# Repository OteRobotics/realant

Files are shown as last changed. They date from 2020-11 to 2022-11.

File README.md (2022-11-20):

RealAnt
=======

The RealAnt robot platform from Ote Robotics is designed for real-world 
reinforcement learning research and development. It is a complete solution 
with a web camera based tracking system. It is aimed to be a low-cost starting
point for anybody interested in bringing reinforcement learning to practical
real robots.

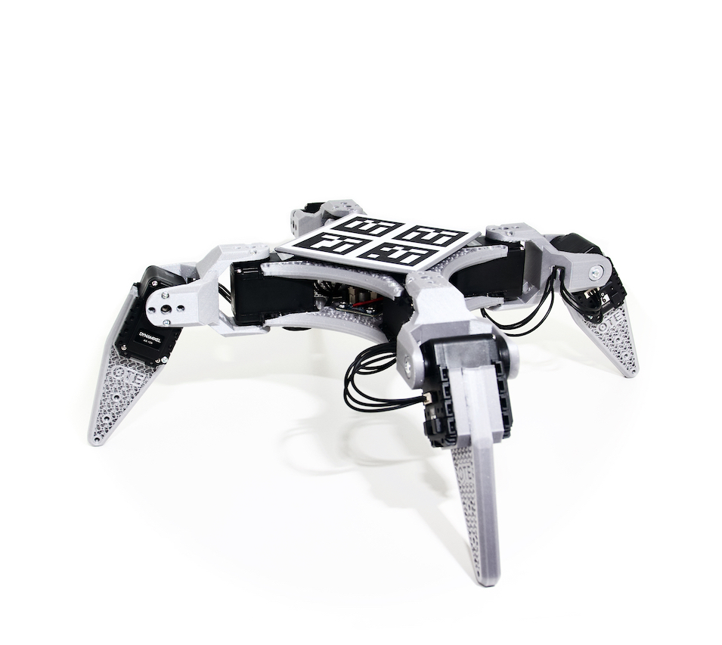
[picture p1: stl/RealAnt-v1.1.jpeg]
RealAnt-v1.1/v1.2


This repository provides 3D models and build instructions
for making your own RealAnt, firmware code for the robot microcontroller, and
Python code for the robot interface and ArUco tag based pose estimation.

If you want to get the robot ready assembled, you can buy them from
<https://shop.oterobotics.com>.

For an example implementation of reinforcement learning that learns
to stand, turn and walking, see <https://github.com/AaltoVision/realant-rl>.

# Getting Started

You can get to reinforcement learning in the real world with five steps:

1. Get or build your own RealAnt.
1. Calibrate and test the web camera for pose estimation.
1. Setup testing scene with adequate lighting.
1. Start Python Server scripts.
1. Start experiments.

## Get Your RealAnt

If you want to get the robot ready assembled, you can buy them from
<https://shop.oterobotics.com>.

To build your own, you need to obtain 8 Robotis Dynamixel AX-12A's and
one Robotis OpenCM9.04A board + accessory set or Ote Robotics RealAnt
Main Board v1.2 with Arduino Nano 33 IoT (see `board_1.2` folder for
PCB gerbers, BOM, layout and schematics PDFs).  

For building, you need additionally some two-wire cable for power, 
a soldering iron, side cutters, a Phillips screwdriver and 
thread-locking fluid (such as Loctite blue).

The 3D model files are under `stl` folder. You need to print two
body torso plates and four leg assemblies.

For PrusaSlicer, use 20% gyroid infill, 0.2mm layer height, no top 
and bottom layers.

## RealAnt Main Board Firmware

For the OpenCM9.04A board, install Arduino and setup Robotis OpenCM9.04 board support,
and then upload the OpenCM9.04 firmware from `ant11_cmd_dxl` folder.

For the Ote Robotics RealAnt Main Board v1.2 with Arduino Nano 33 IoT, 
install Arduino and use firmware from `ant14_cmd_dxl_nano33iot` folder.
You also need to install the forked DynamixelSDK from this folder into
Arduino libraries.

## Pose Estimation Calibration and Testing

Print calibration chessboard from `markers` on
e.g. A4 and glue them to a flat surface (e.g. piece of cardboard). 
Print the calibration chessboard at 100% scale, this
produces 4cm chessboard pattern. (If you use a different scaling, change
`calibrate_camera.py` script's marker size accordingly.)
Clipping at the edges of the outermost squares doesn't matter,
as only the inner corners of the squares are used.

Capture various poses of the chessboard (15+ images)
with `capture.py` and then run `calibrate_camera.py`.
Move the position of the chessboard around, so that it would
cover the whole field of view of the camera. Tilting
the chessboard also can yield better calibration.
Make sure your chessboard poses are free from motion blur,
delete the ones that are blurry.

After this, run `calibrate_camera.py` to obtain `cam_calib.pkl` file.

```
# mkdir CAMERANAME
# cd CAMERANAME
# python ../capture.py
# python ../calibrate_camera.py 
```

After calibrating the camera, adjust `showaruco_board.py` such
that it uses the correct `cam_calib.pkl` file.

Print and attach reference and moving agent markers to 
floor and the ant, adjust their sizes in the `showaruco_board.py` script
and run the script to estimate distance. Make sure to use correct
camera calibration file.

```
# python showaruco_board.py
```

## Setup The Test Scene

Make sure you have adequate lighting so that there is no motion blur in
pose estimation during robot movement.

For example, 2x 50W LED floodlights rated at 3800 lumens 
mounted 1 m above the robot should yield around 3000 lux illuminance
at the robot level, which is enough for reinforcement learning purposes
with Logitech Brio 4K USB camera.

## Python Interface Server

For starting trials, start the following scripts in their own terminal windows:

```
# python antproxy.py         # zmq pub-sub communication proxy
# python ant_server.py       # server for serial communication to the physical ant
# python showaruco_board.py  # pose estimation
```

You might need to adjust `ant_server.py` for the correct serial port device.
It defaults to `/dev/ttyACM0` on Linux.

Test scripts:

```
# python ant_send_cmd.py     # send simple test movements to ant
```

## Reinforcement Learning

For an example implementation of reinforcement learning that learns
to stand, turn and walking, see https://github.com/AaltoVision/realant-rl.

Clone that repository, and then run the scripts:

```
# rollout_server.py             # random exploration & agent evaluation
# train_client.py --task walk   # train for walking
```

# Further Interface Implementation Details

The main components are

 * `antproxy.py` (the main pub-sub network proxy, this should work as-is, as it just receives and forwards packages as a message hub — just run this on the background),
 * `showaruco_board.py` (this sends orientation and location info) and
 * `ant_server.py` (this processes the s1...s8 servo commands, and sends joint position values and (optional) foot sensors).
 
The pub-sub network protocol is very simple.
Each message is a list of byte strings.
The beginning of the first string is the "topic" in ZMQ terms
(used with `zmq.SUBSCRIBE` to filter in messages, `""` receives everything):

 * `"cmd"` is a command that the `ant_server.py` receives. This takes a 
   multipart string argument that is forwarded to the firmware. 
   Currently supported commands are `"sN X sM Y ..."` where N,M = servo number
   in [1,8] and X,Y = angle setpoint in [224...800], 512 = middle,
   and `"reset"`, `"attach_servos"` and `"detach_servos"`.
 * `"{"` which is json data, which is used both for all measurements 
   (and recorded setpoints) from `ant_server.py` and also for 
   `showaruco_board.py` measurement packets.

# RealAnt Revision History

| Version | Description |
| --- | --- |
| RealAnt v1 | First version with FP04-2 hip joints and OpenCM9.04 microcontroller board |
| RealAnt v1.1 | Hip joints replaced with 3D printed ones, OpenCM9.04 microcontroller board |
| RealAnt v1.2 | Microcontroller board changed to Arduino Nano 33 IoT based one |

# Copyright and License

Unless otherwise noted, all source code, documentation and data in this
repository is Copyright (c) 2020 Ote Robotics Ltd and is licensed under
MIT license.

See LICENSE for details.

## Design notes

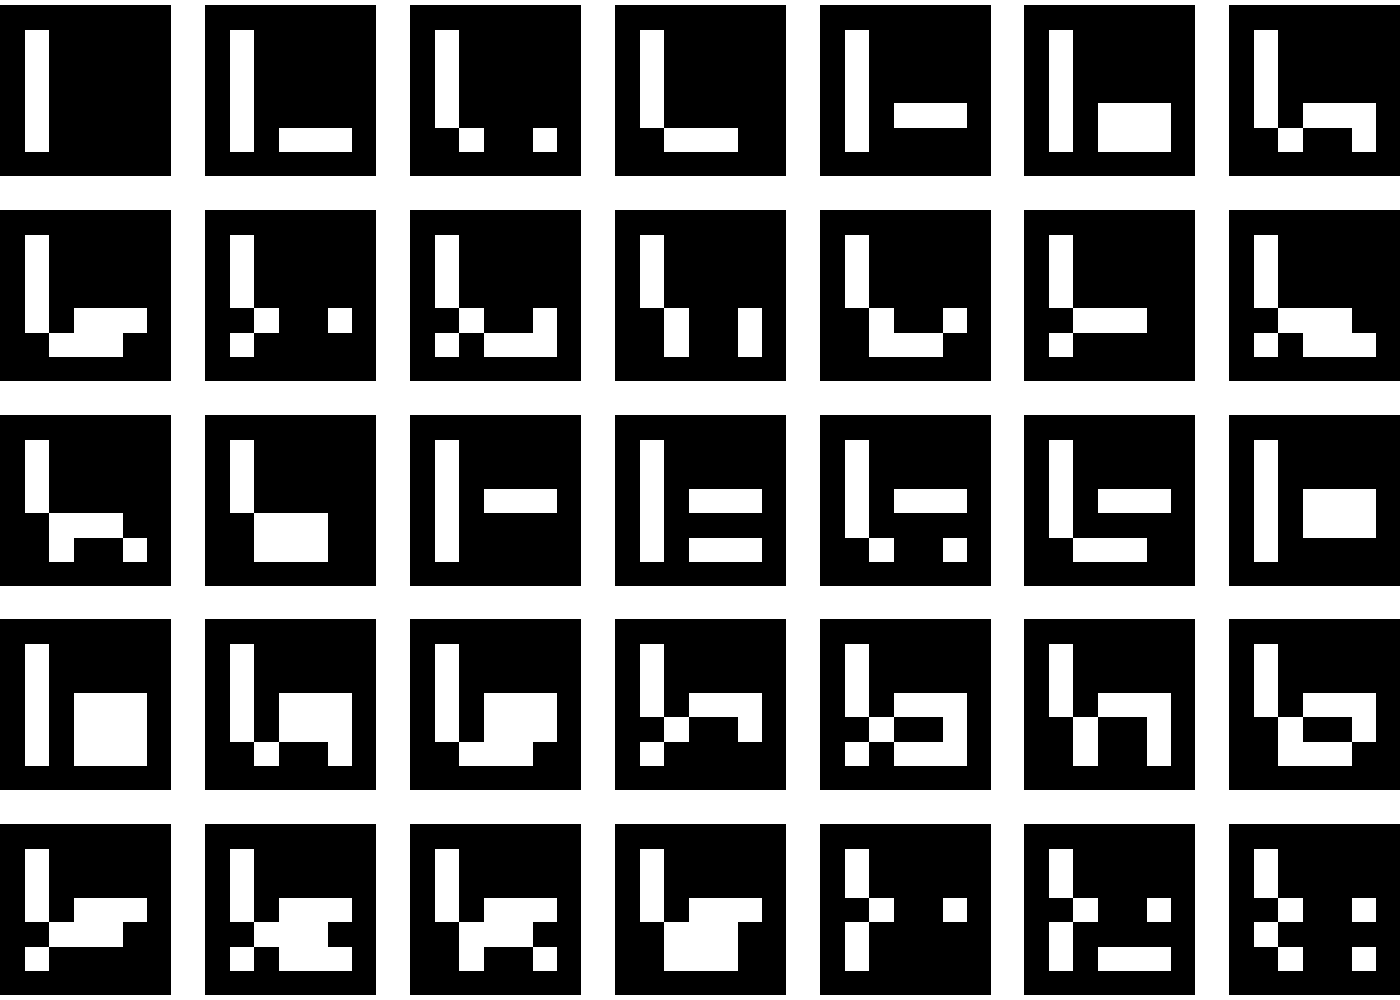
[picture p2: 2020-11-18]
markers/aruco_gridboard_big.png

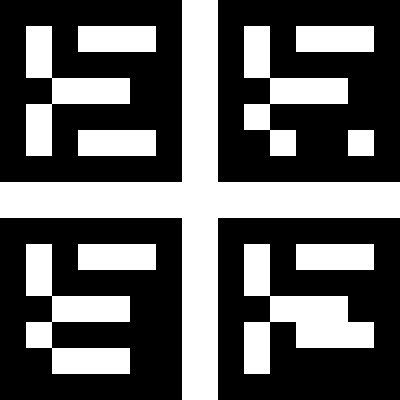
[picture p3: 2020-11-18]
markers/aruco_gridboard_small.png

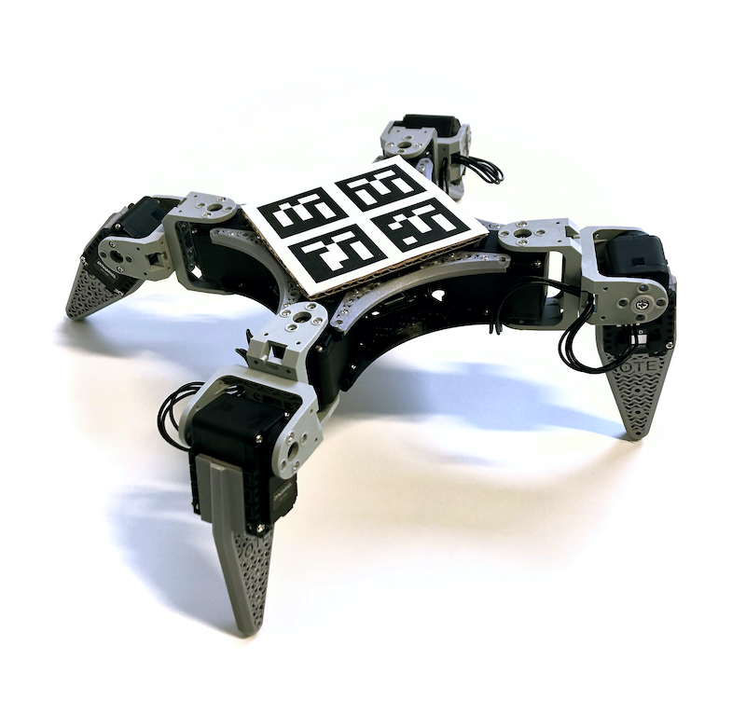
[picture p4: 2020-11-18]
stl/RealAnt-v1.jpeg

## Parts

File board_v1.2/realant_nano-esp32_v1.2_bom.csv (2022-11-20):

Source: | realant_nano_esp32.kicad_sch
Date: | 2022 August 14, Sunday 13:06:41
Tool: | Eeschema (6.0.0-0)
Generator: | /Applications/KiCad/KiCad.app/Contents/SharedSupport/plugins/bom_csv_grouped_by_value.py
Component Count: | 16
Individual Components:
Item | Qty | Reference(s) | Value | LibPart | Footprint | Datasheet
 |  | C1 | 0.1uF | Device:C | Capacitor_SMD:C_0805_2012Metric_Pad1.18x1.45mm_HandSolder | ~
 |  | C2 | 220uF | Device:C_Polarized | Capacitor_THT:CP_Radial_D6.3mm_P2.50mm | ~
 |  | C3 | 220uF | Device:C_Polarized | Capacitor_THT:CP_Radial_D6.3mm_P2.50mm | ~
 |  | J1 | DXL_CONN | connector:DXL_CONN | Connector_JST:JST_EH_B3B-EH-A_1x03_P2.50mm_Vertical
 |  | J2 | DXL_CONN | connector:DXL_CONN | Connector_JST:JST_EH_B3B-EH-A_1x03_P2.50mm_Vertical
 |  | J3 | DXL_CONN | connector:DXL_CONN | Connector_JST:JST_EH_B3B-EH-A_1x03_P2.50mm_Vertical
 |  | J4 | DXL_CONN | connector:DXL_CONN | Connector_JST:JST_EH_B3B-EH-A_1x03_P2.50mm_Vertical
 |  | R1 | 10k | Device:R | Resistor_SMD:R_0805_2012Metric_Pad1.20x1.40mm_HandSolder | ~
 |  | R2 | 10k | Device:R | Resistor_SMD:R_0805_2012Metric_Pad1.20x1.40mm_HandSolder | ~
 |  | R3 | 10k | Device:R | Resistor_SMD:R_0805_2012Metric_Pad1.20x1.40mm_HandSolder | ~
 |  | R4 | 5.1k | Device:R | Resistor_SMD:R_0805_2012Metric_Pad1.20x1.40mm_HandSolder | ~
 |  | U1 | ESP32-DevKitC | ESP32-Boards:ESP32-DevKitC | Espressif:ESP32-DevKitC | https://docs.espressif.com/projects/esp-idf/zh_CN/latest/esp32/hw-reference/esp32/get-started-devkitc.html
 |  | U2 | Arduino-NANO-33 | nano33iot:Arduino-NANO-33 | nano33iot:NANO_33_Socket | ~
 |  | U3 | 74LVC2G241DC | ICs:74LVC2G241DC | Package_SO:SSOP-8_2.95x2.8mm_P0.65mm | https://www.mouser.fi/datasheet/2/916/74LVC2G241-1319835.pdf
 |  | U4 | PWR_CONN | connector:PWR_CONN | Connector_Molex:Molex_Micro-Fit_3.0_43650-0200_1x02_P3.00mm_Horizontal
 |  | U5 | NCP1117-5.0_SOT223 | Regulator_Linear:NCP1117-5.0_SOT223 | Package_TO_SOT_SMD:SOT-223-3_TabPin2 | http://www.onsemi.com/pub_link/Collateral/NCP1117-D.PDF
Collated Components:
Item | Qty | Reference(s) | Value | LibPart | Footprint | Datasheet
1 | 1 | C1 | 0.1uF | Device:C | Capacitor_SMD:C_0805_2012Metric_Pad1.18x1.45mm_HandSolder | ~
2 | 2 | C2, C3 | 220uF | Device:C_Polarized | Capacitor_THT:CP_Radial_D6.3mm_P2.50mm | ~
3 | 4 | J1, J2, J3, J4 | DXL_CONN | connector:DXL_CONN | Connector_JST:JST_EH_B3B-EH-A_1x03_P2.50mm_Vertical
4 | 3 | R1, R2, R3 | 10k | Device:R | Resistor_SMD:R_0805_2012Metric_Pad1.20x1.40mm_HandSolder | ~
5 | 1 | R4 | 5.1k | Device:R | Resistor_SMD:R_0805_2012Metric_Pad1.20x1.40mm_HandSolder | ~
6 | 1 | U1 | ESP32-DevKitC | ESP32-Boards:ESP32-DevKitC | Espressif:ESP32-DevKitC | https://docs.espressif.com/projects/esp-idf/zh_CN/latest/esp32/hw-reference/esp32/get-started-devkitc.html
7 | 1 | U2 | Arduino-NANO-33 | nano33iot:Arduino-NANO-33 | nano33iot:NANO_33_Socket | ~
8 | 1 | U3 | 74LVC2G241DC | ICs:74LVC2G241DC | Package_SO:SSOP-8_2.95x2.8mm_P0.65mm | https://www.mouser.fi/datasheet/2/916/74LVC2G241-1319835.pdf
9 | 1 | U4 | PWR_CONN | connector:PWR_CONN | Connector_Molex:Molex_Micro-Fit_3.0_43650-0200_1x02_P3.00mm_Horizontal
10 | 1 | U5 | NCP1117-5.0_SOT223 | Regulator_Linear:NCP1117-5.0_SOT223 | Package_TO_SOT_SMD:SOT-223-3_TabPin2 | http://www.onsemi.com/pub_link/Collateral/NCP1117-D.PDF

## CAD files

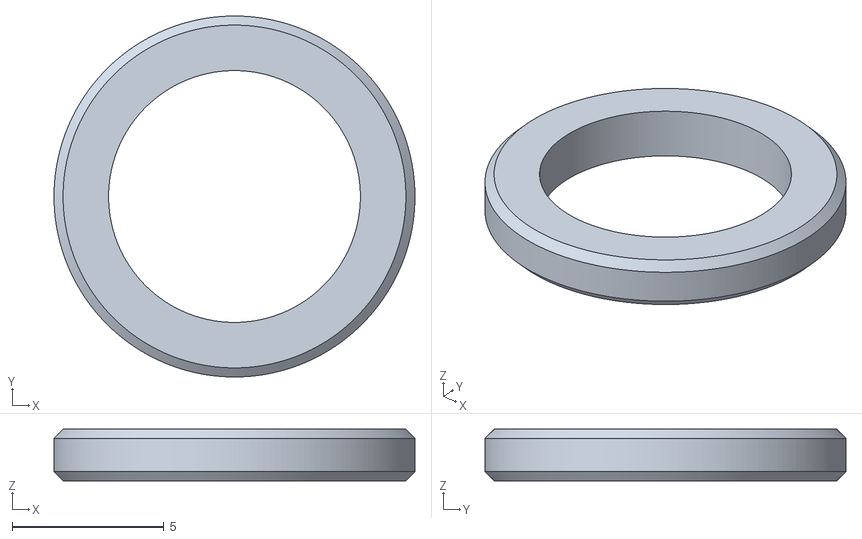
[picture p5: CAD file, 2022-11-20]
stl/joint_spacer_ring.stl
11.9 x 11.9 x 1.70

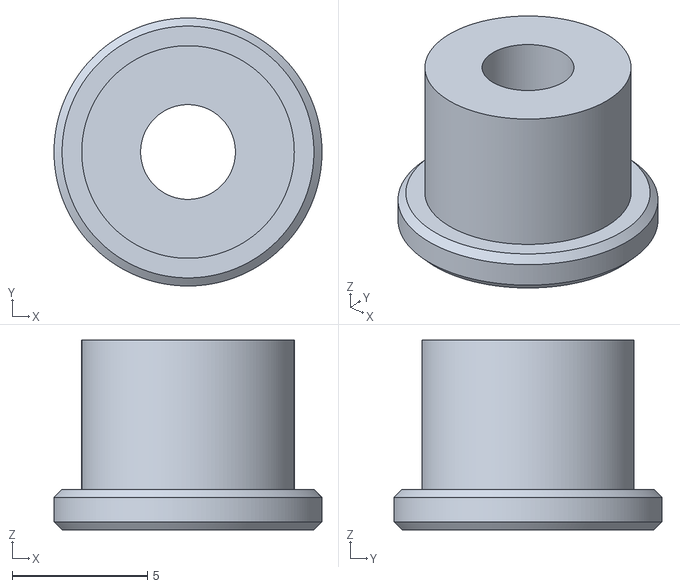
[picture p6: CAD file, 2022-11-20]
stl/joint_slide_bearing.stl
9.90 x 9.90 x 7.01

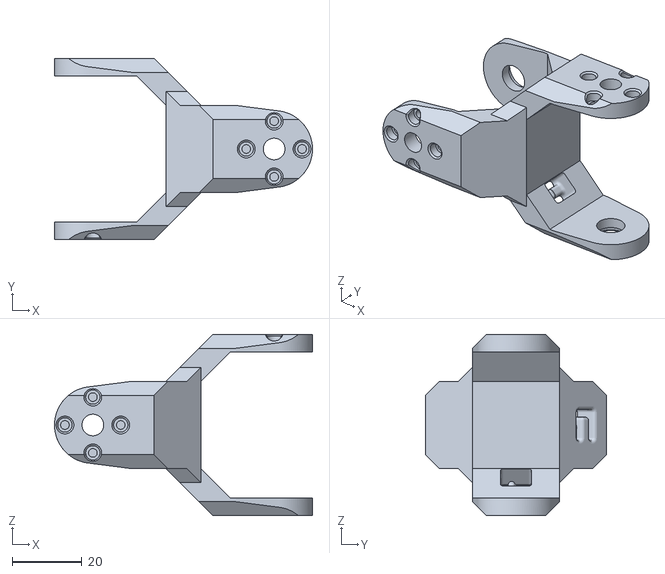
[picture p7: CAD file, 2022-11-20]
stl/hip_joint_v26.stl
74.0 x 52.0 x 52.0

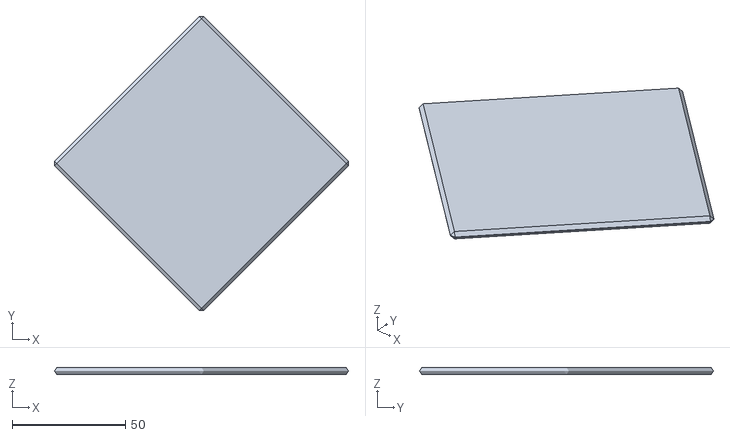
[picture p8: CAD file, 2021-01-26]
stl/tag_plate_v14.stl
129.9 x 129.9 x 3.00

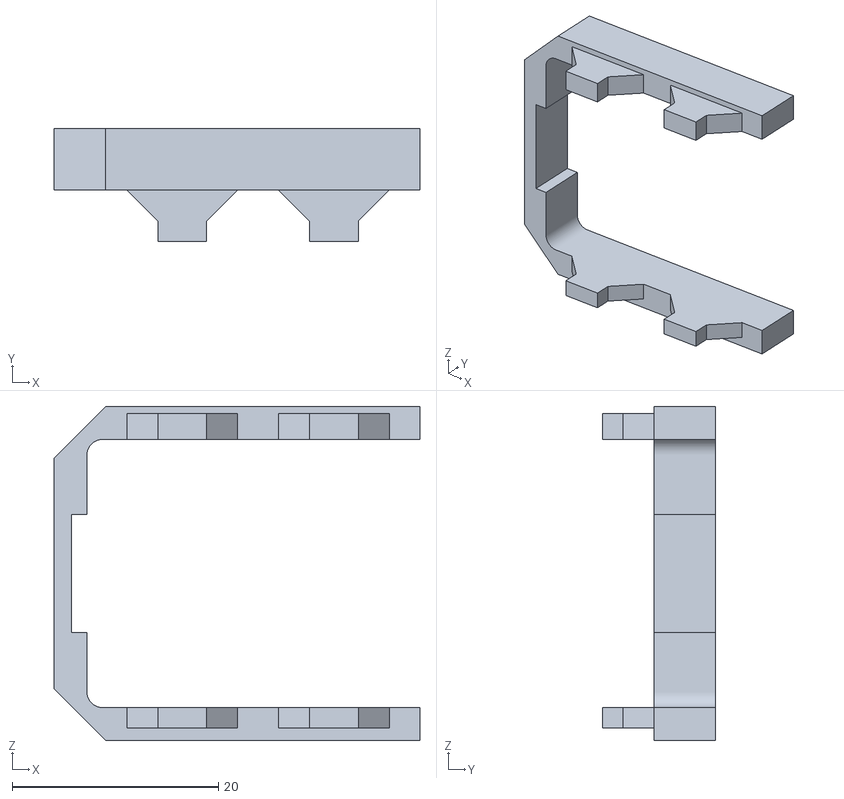
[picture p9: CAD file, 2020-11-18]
stl/leg_spacer_v8.stl
35.5 x 11.0 x 32.4

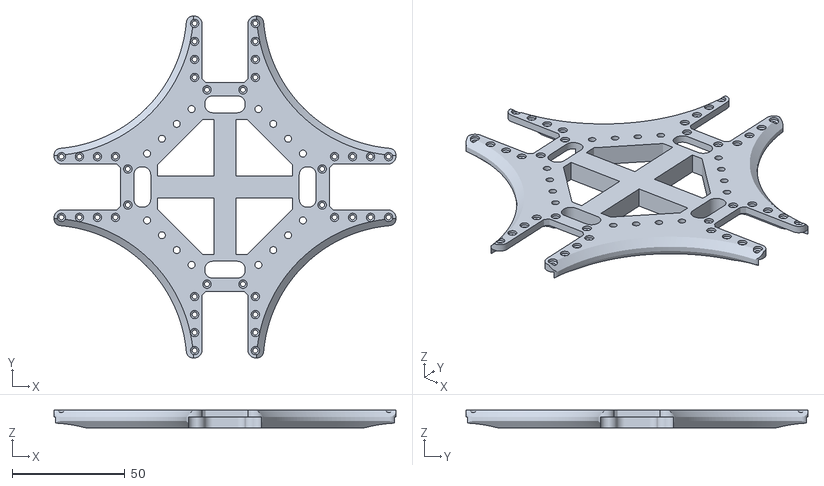
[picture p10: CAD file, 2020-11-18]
stl/body_v6.stl
152.0 x 152.0 x 8.00

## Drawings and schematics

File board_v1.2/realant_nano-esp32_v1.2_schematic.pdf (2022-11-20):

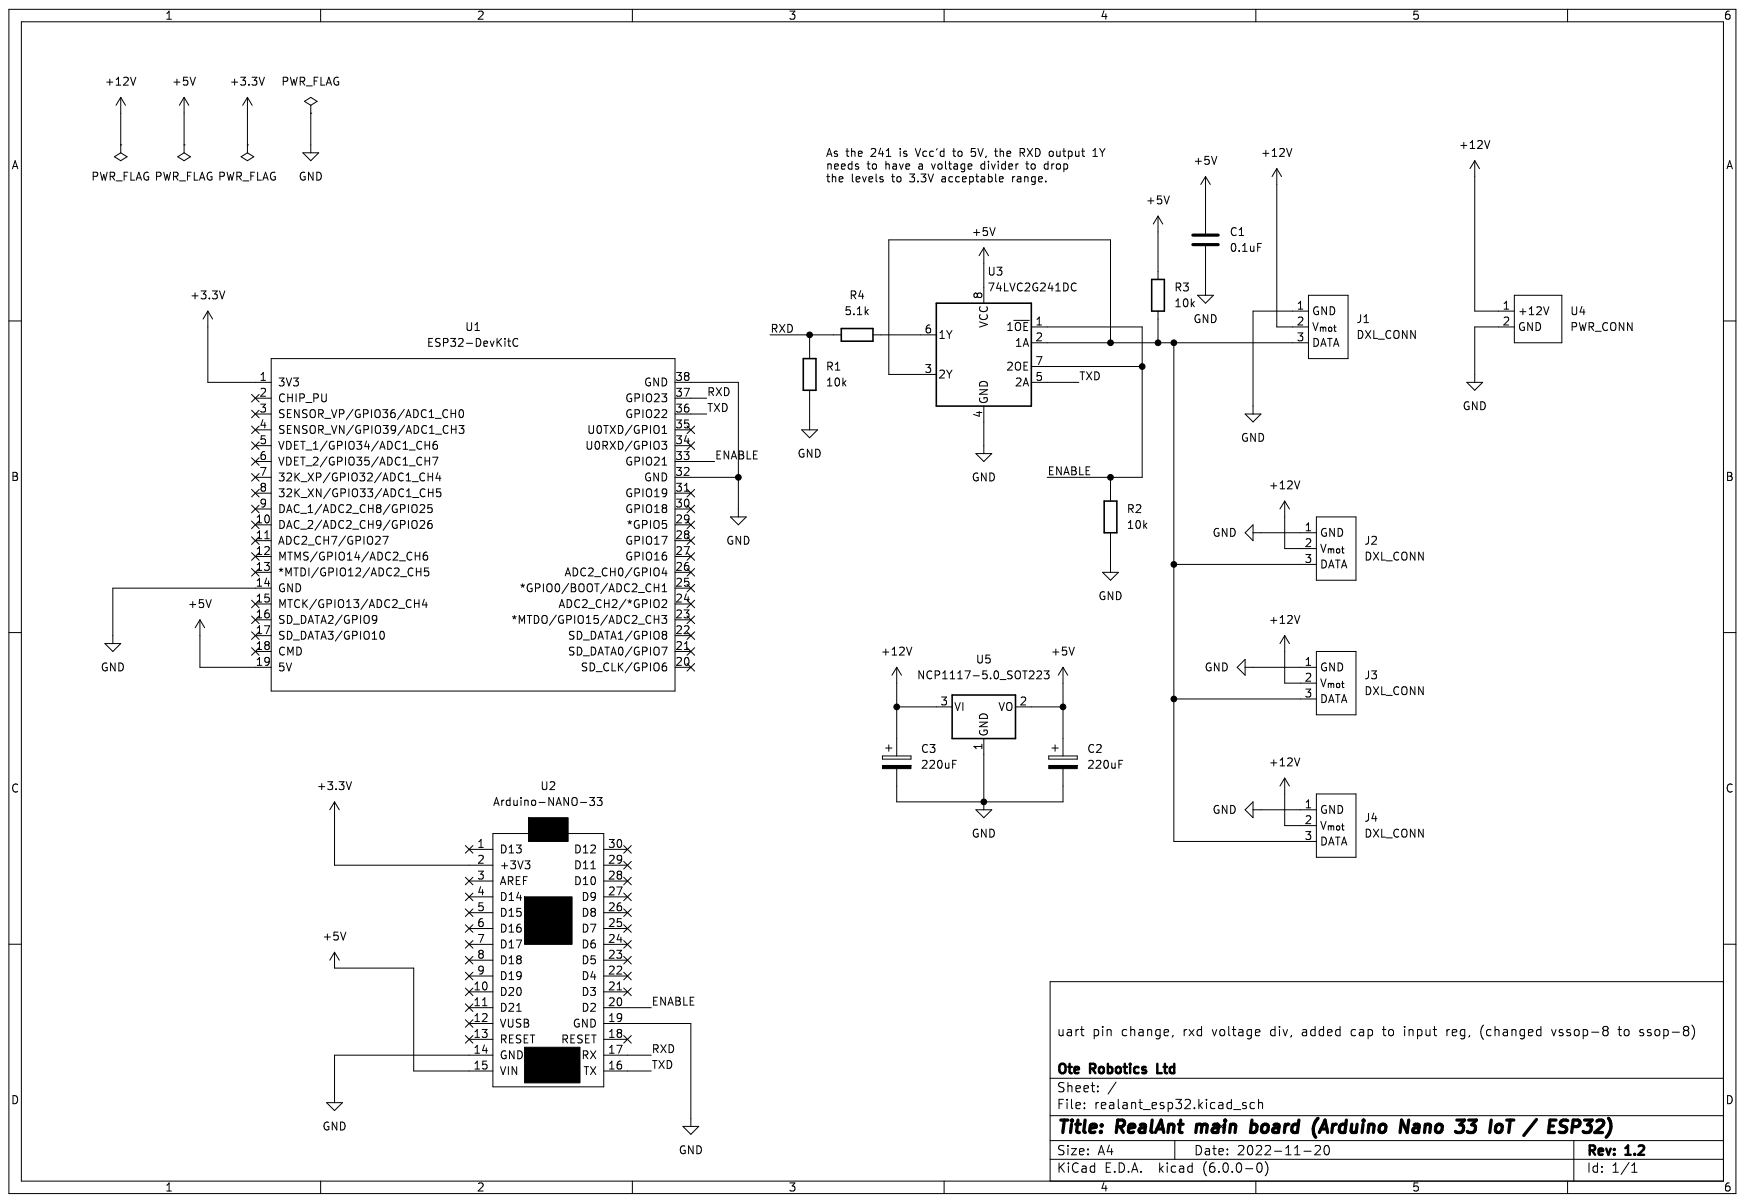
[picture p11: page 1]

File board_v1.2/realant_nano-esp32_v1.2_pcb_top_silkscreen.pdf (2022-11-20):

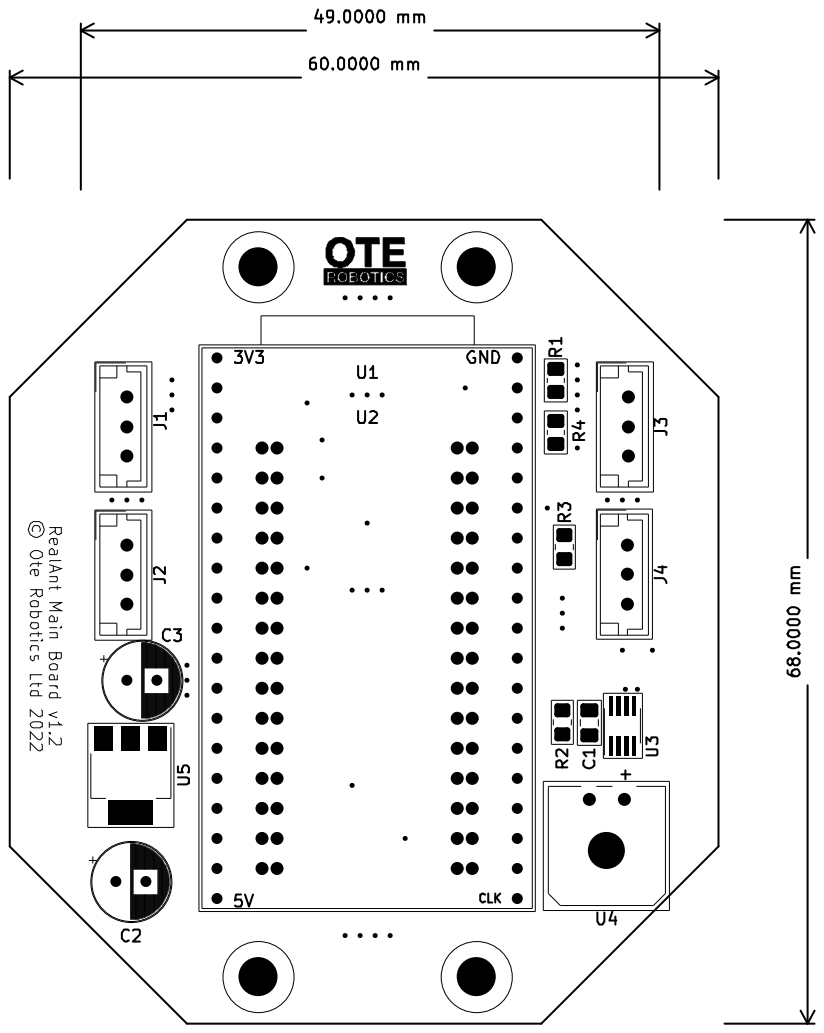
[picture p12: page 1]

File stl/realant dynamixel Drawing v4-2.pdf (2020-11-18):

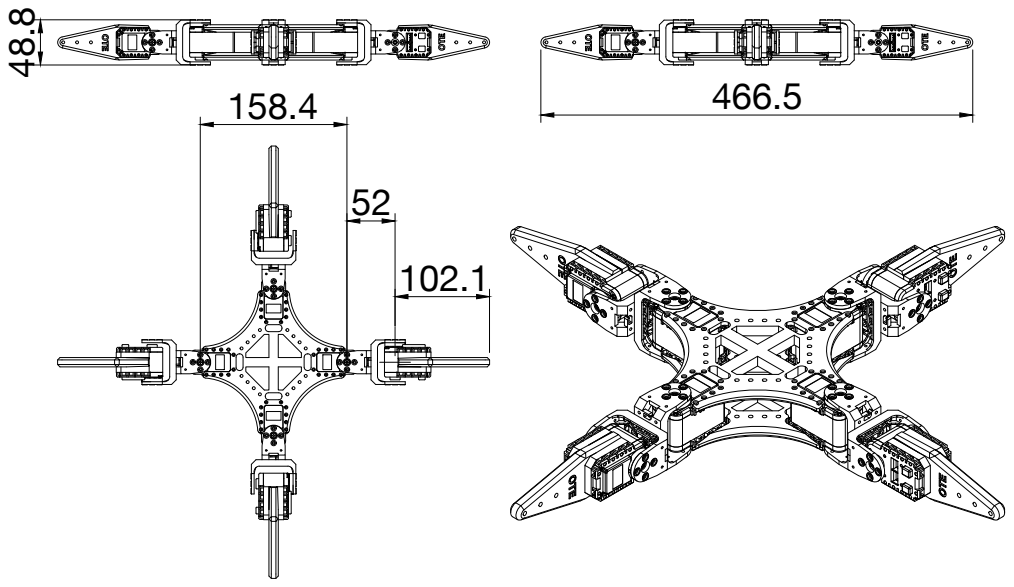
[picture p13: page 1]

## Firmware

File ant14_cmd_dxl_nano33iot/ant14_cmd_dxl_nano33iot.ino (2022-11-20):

// log: 
//  20180114 - the ant has risen! all the servos turning at once consume about 4A @ 5V (!)  teensy 3.5 version
//  20180819 - hw functions properly
//  20180821 - cmd interface
//  20181218 - added feet contact pins
//  20190329 - added serial1 for bt connectivity
//  20200423 - build fixes for arduino 1.8.12 teensyduino 1.51
//  20201022 - dynamixel version
//  20210119 - temp read improvements
//  20220709 - arduino nano 33 iot + realant mainboard v1.1 works, requires modified dynamixelsdk library

//#include <DynamixelWorkbench.h>
#include <DynamixelSDK.h>

// AX-series Control table address
#define ADDR_AX_TORQUE_ENABLE           24                 // Control table address is different in Dynamixel model
#define ADDR_AX_GOAL_POSITION           30
#define ADDR_AX_TORQUE_LIMIT            34
#define ADDR_AX_PRESENT_POSITION        36
#define ADDR_AX_PRESENT_TEMPERATURE     43

// Protocol version
#define PROTOCOL_VERSION                1.0                 // See which protocol version is used in the Dynamixel




#define DEVICE_NAME "1" //Dynamixel on Serial1 (Arduino Nano 33 IoT)

#define BAUDRATE  1000000



int servopos[] = {512, 512, 512, 512, 512, 512, 512, 512};


// feet contact pins 33-36 (plywood), (white ant pins 29-32)

//const int feet_contact_pins[] = {29,30,31,32};

String inputString = "";         // a String to hold incoming data
bool stringComplete = false;  // whether the string is complete

dynamixel::PortHandler *portHandler = NULL;
dynamixel::PacketHandler *packetHandler = NULL;

int read_servo_i = 1;
int servo_temps[] = {0,0,0,0, 0,0,0,0};

void read_servo_positions()
{
  int dxl_comm_result = COMM_TX_FAIL;
  uint8_t dxl_error = 0;  
  const char *log;

  uint8_t pos_failures = 0;
  uint8_t temp_failures = 0;

  bool result = false;

    //unsigned long start_read = millis();

    Serial.print("meas ");

    Serial.print(millis());
    Serial.print("\t");

  
    for (int i = 1; i <= 8; i++) {
      uint16_t get_data = servopos[i-1]; // backup estimate

      dxl_comm_result = packetHandler->read2ByteTxRx(portHandler, i, ADDR_AX_PRESENT_POSITION, (uint16_t*)&get_data, &dxl_error);
      if (dxl_comm_result != COMM_SUCCESS)
      {
        pos_failures |= 1<<(i-1);
      }

      Serial.print(get_data);
      Serial.print("\t");
    }


    for (int i = 0; i < 8; i++) {
      Serial.print(servopos[i]);
      Serial.print("\t");
    }

    for (int i = 0; i < 4; i++) {
      Serial.print(0); //not digitalRead(feet_contact_pins[i]));
      Serial.print("\t");
    }

    // temps, read one servo per cycle to speed up cycle time
    {
      int8_t get_data = 0;
  
      dxl_comm_result = packetHandler->read1ByteTxRx(portHandler, read_servo_i, ADDR_AX_PRESENT_TEMPERATURE, (uint8_t*)&get_data, &dxl_error);
      if (dxl_comm_result != COMM_SUCCESS)
      {
        Serial.println("- Failed to get present temperature");
        temp_failures |= 1<<(read_servo_i-1);
      } else {
        servo_temps[read_servo_i-1] = get_data;
      }
  
      read_servo_i++;
      if (read_servo_i == 9)
        read_servo_i = 1;
        
      for (int i = 1; i <= 8; i++) {
        Serial.print(servo_temps[i-1]);
        Serial.print("\t");
      }
    }

    Serial.print("\t");
    Serial.print(freeMemory());
    
    Serial.println();

    //Serial.print("- read took ");
    //Serial.println((millis() - start_read));


    if (pos_failures > 0)
    {
        Serial.print("- Failed to get present position 0x");
        Serial.println(pos_failures, HEX);  
    }
    if (temp_failures > 0)
    {
        Serial.print("- Failed to get present temperature 0x");
        Serial.println(temp_failures, HEX);  
    }    
}

unsigned long last_time_millis = 0;

void setup() {
    int dxl_comm_result = COMM_TX_FAIL;
    uint8_t dxl_error = 0;
    const char *log;
    bool result = false;

    portHandler = dynamixel::PortHandler::getPortHandler(DEVICE_NAME);
    packetHandler = dynamixel::PacketHandler::getPacketHandler(PROTOCOL_VERSION);


    inputString.reserve(200);

    Serial.begin(115200);
    while(!Serial);
    Serial.println("realant says hello - ant14_cmd_dxl 2022-07-09");

#if defined(__SAMD21G18A__)
#if defined(SAMD_NANO_33_IOT)
    Serial.println("arduino nano 33 iot")
#endif
    Serial.println("samd21g18a");
#endif
    delay(1000);

    // Open port
    if (portHandler->openPort())
    {
      Serial.print("- Succeeded to open the Dynamixel port\n");
    }
    else
    {
      Serial.print("- Failed to open the Dynamixel port\n");
    }
  
    // Set port baudrate
    if (portHandler->setBaudRate(BAUDRATE))
    {
      Serial.print("- Succeeded to change the baudrate\n");
    }
    else
    {
      Serial.print("- Failed to change the baudrate\n");
    }

    for (int i = 1; i <= 8; i++) {

        dxl_comm_result = packetHandler->write2ByteTxRx(portHandler, i, ADDR_AX_TORQUE_LIMIT, 512, &dxl_error);
        if (dxl_comm_result != COMM_SUCCESS)
        {
          packetHandler->getTxRxResult(dxl_comm_result);
          Serial.print("- id: ");
          Serial.print(i);
          Serial.println("- Failed set torque limit (1)");
          
        }
        else if (dxl_error != 0)
        {
          packetHandler->getRxPacketError(dxl_error);
          Serial.print("- id: ");
          Serial.print(i);
          Serial.println("- Failed set torque limit (2)");
        }
        else
        {
          Serial.print("- id: ");
          Serial.print(i);
          Serial.println("- Succeeded to set torque limit");
        }
    }
      
}

String getValue(String data, char separator, int index)
{
    int found = 0;
    int strIndex[] = { 0, -1 };
    int maxIndex = data.length() - 1;

    for (int i = 0; i <= maxIndex && found <= index; i++) {
        if (data.charAt(i) == separator || i == maxIndex) {
            found++;
            strIndex[0] = strIndex[1] + 1;
            strIndex[1] = (i == maxIndex) ? i+1 : i;
        }
    }
    return found > index ? data.substring(strIndex[0], strIndex[1]) : "";
}



void loop() {

  int dxl_comm_result = COMM_TX_FAIL;
  uint8_t dxl_error = 0;
  
  const char *log;
  bool result = false;

  while (Serial.available()) {
    char inChar = (char)Serial.read();
    inputString += inChar;
    if (inChar == '\n') {
      stringComplete = true;
    }
  }
  
  if (stringComplete) {
    Serial.print("- recv: ");
    Serial.println(inputString);

    if (inputString.startsWith("attach_servos")) {
      for (int i = 1; i <= 8; i++) {
        //result = dxl_wb.jointMode(i, 0, 0, &log);
        //if (result == false)
        //{
        //  Serial.println(log);
        //  Serial.println("- Failed to change joint mode");
        //}
        //else
        //{
        //  Serial.println("- Succeeded to change joint mode");
        //} 

        
        //result = dxl_wb.torqueOn(i, NULL);
        dxl_comm_result = packetHandler->write1ByteTxRx(portHandler, i, ADDR_AX_TORQUE_ENABLE, 1, &dxl_error);

        if (dxl_comm_result != COMM_SUCCESS)
        {
          Serial.println("- Failed to change torque on");
        }
        else
        {
          Serial.println("- Succeeded to change torque on");
        } 
      }
    }
    else if (inputString.startsWith("detach_servos")) {
      for (int i = 1; i <= 8; i++) {
        dxl_comm_result = packetHandler->write1ByteTxRx(portHandler, i, ADDR_AX_TORQUE_ENABLE, 0, &dxl_error);

        if (dxl_comm_result != COMM_SUCCESS)
        {
          Serial.println("- Failed to change torque off");
        }
        else
        {
          Serial.println("- Succeeded to change torque off");
        } 
      }
    }
    else if (inputString.startsWith("reset")) {
      for (int i = 1; i <= 8; i++) {
        servopos[i-1] = 512;
        dxl_comm_result = packetHandler->write2ByteTxRx(portHandler, i, ADDR_AX_GOAL_POSITION, servopos[i-1], &dxl_error);
        if (dxl_comm_result != COMM_SUCCESS)
        {
          Serial.println("- Failed to set goal position (reset)");
        }
      }
    }
    else if (inputString.startsWith("standup")) {
      for (int i = 1; i <= 8; i++) {
        int val = (i % 2 == 1) ? 512 : 224;
        servopos[i-1] = val;
        dxl_comm_result = packetHandler->write2ByteTxOnly(portHandler, i, ADDR_AX_GOAL_POSITION, servopos[i-1]);
        if (dxl_comm_result != COMM_SUCCESS)
        {
          Serial.println("- Failed to set goal position (standup)");
        }
      }
      
    }
    else {
      //unsigned long start_write = millis();
  
      for (int i = 0; i < 8; i++) {
        String k = getValue(inputString, ' ', 2*i);
        String v = getValue(inputString, ' ', 2*i+1);
  
        if (k != "" && k.startsWith("s"))
        {
          int s = k.substring(1).toInt();
          if (v != "" && (s >= 1 && s <= 8))
          {
            int pos =  v.toInt();
            //Serial.print("- driving servo ");
            //Serial.print(s);
            //Serial.print(" to pos ");
            //Serial.println(pos);
            servopos[s-1] = pos;
            
            dxl_comm_result = packetHandler->write2ByteTxOnly(portHandler, s, ADDR_AX_GOAL_POSITION, servopos[s-1]);
            if (dxl_comm_result != COMM_SUCCESS)
            {
              Serial.println("- Failed to set goal position (standup)");
            }
          }
        }
      }

      //Serial.print("- write took ");
      //Serial.println((millis() - start_write));
    }



    // clear the string:
    inputString = "";
    stringComplete = false;
  }

  if ((millis() - last_time_millis) > 20) {
    read_servo_positions();
    last_time_millis = millis();
  }
}


#ifdef __arm__
// should use uinstd.h to define sbrk but Due causes a conflict
extern "C" char* sbrk(int incr);
#else  // __ARM__
extern char *__brkval;
#endif  // __arm__

int freeMemory() {
  char top;
#ifdef __arm__
  return &top - reinterpret_cast<char*>(sbrk(0));
#elif defined(CORE_TEENSY) || (ARDUINO > 103 && ARDUINO != 151)
  return &top - __brkval;
#else  // __arm__
  return __brkval ? &top - __brkval : &top - __malloc_heap_start;
#endif  // __arm__
}

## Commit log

2020-11-18 Initial release
    [body_v6.stl, leg_spacer_v8.stl, leg_v8.stl]
2021-01-26 Add a new 3D-printable tag plate
    * Can be used for gluing the Aruco agent tag on the RealAnt instead of
    cardboard.
    * Print settins: 20% gyroid infill, no bottom layer.
    * Fix to the RealAnt with velcro tape bits.
    [tag_plate_v14.stl]
2021-03-22 Refactor tracking code to separate files and use OpenCV for camera tweaks in Windows
2022-11-20 Add RealAnt v1.2 board and v1.1/v1.2 STL files
    * Released PCB gerbers, BOM and schematic for
    Arduino Nano 33 IoT based Ote Robotics
    RealAnt Main Board v1.2.
    * Added updated firmware package for the above.
    * Added STL files for hip joints and joint slide
    bearings.
    [hip_joint_v26.stl, joint_slide_bearing.stl, joint_spacer_ring.stl, realant_esp32-B_Cu.gbr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]
2023-01-05 Add board drill files
    [realant_esp32-NPTH.drl, realant_esp32-PTH.drl]
